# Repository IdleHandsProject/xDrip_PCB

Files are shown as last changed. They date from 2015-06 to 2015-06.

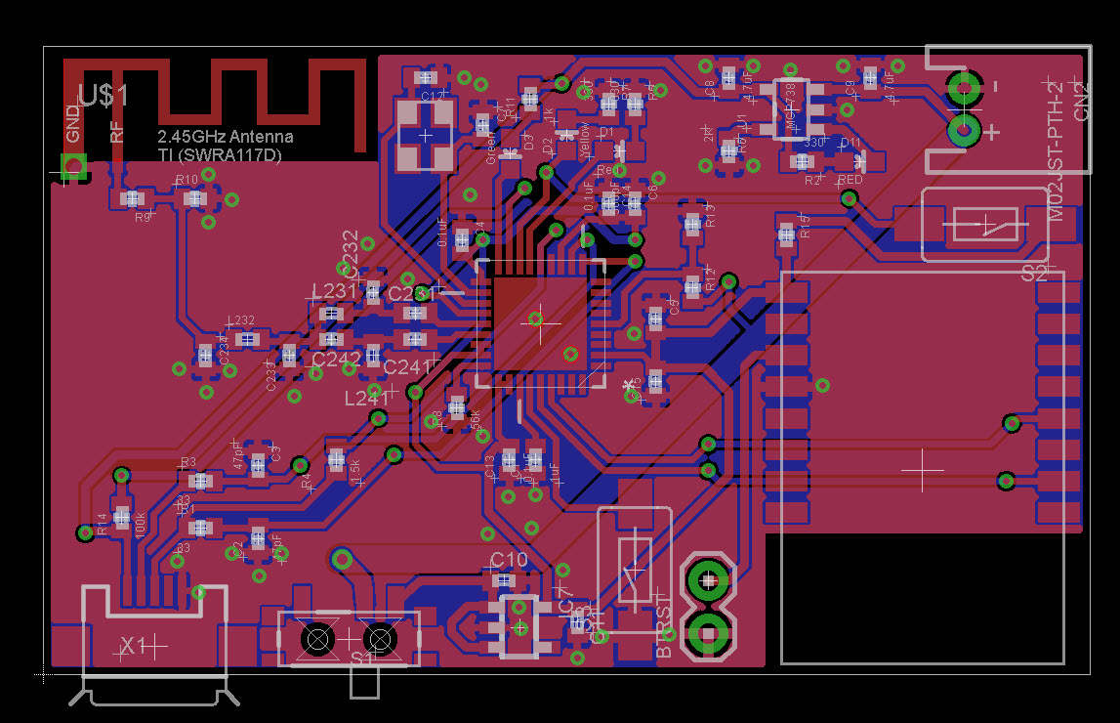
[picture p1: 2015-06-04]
DexDripLayout.jpg

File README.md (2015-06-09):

# xDrip_PCB

A custom PCB for the xDrip Project
<p>The xDrip project can be found here: http://stephenblackwasalreadytaken.github.io/xDrip/
Note: This board has not been tested. It is a WIP.
<p>Please don't go blindly ordering a board and expecting it to work. Go over the schematics yourself and confirm everything is correct. I will post an update when I have a working version.
<p>I am also working on a 3D printed case that will be available on shapeways, and I will be looking into mass producing the boards to reduce the costs. They will be fully completed boards. 
<p>I post updates on Twitter:  <a href="http://www.twitter.com/idlehandsdev">@idlehandsdev</a>

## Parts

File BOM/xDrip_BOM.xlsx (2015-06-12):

Qty | Value | Package | Parts | DIGIKEY PROD_ID
1 |  | SWITCH-SPST-SMD-A | S1 | 563-1102-1-ND
6 | 0.1uF | C0402 | C4, C5, C13, C14, C10, C11 | 587-1227-1-ND
3 | 1.2nH | C0402 | L231, L232, L241 | 587-1499-1-ND
1 | 1.5k | 0402-RES | R4 | P1.50KLCT-ND
1 | 1.5pF | 0402-CAP | C234 | 490-6213-1-ND
1 | 1.8pF | 0402-CAP | C233 | 712-1271-1-ND
1 | 100k | 0402-RES | R14 | P100KJCT-ND
2 | 100pF | 0402-CAP | C231, C241 | 490-5922-1-ND
1 | 1M | 0402-RES | R13 | P1.00MLCT-ND
1 | 1k | 0402-RES | R11 | P1.0KJCT-ND
2 | 1pF | 0402-CAP | C232, C242 | 587-1007-1-ND
1 | 1uF | 0402-CAP | C1 | 490-1320-1-ND
1 | 2K | 0402-RES | R6 | P2.00KLCT-ND
2 | 33 | 0402-RES | R1, R3 | P33.0LCT-ND
6 | 330 | 0402-RES | R2, R5, R7, R9, R10, R15 | RMCF0402JT330RCT-ND
2 | 33pF | 0402-CAP | C7, C12 | 490-5936-1-ND
2 | 4.7uF | 0402-CAP | C8, C9 | 490-5915-1-ND
1 | 470K | 0402-RES | R12 | RHM470KCDCT-ND
2 | 47pF | 0402-CAP | C2, C3 | 399-7796-1-ND
1 | 48mHz Abracon | 3.2X2.5MM | Y1 | 535-10282-1-ND
2 | 560pF | 0402-CAP | C6, C15 | 1276-1577-1-ND
1 | 56k | 0402-RES | R8 | RHM56.0KCDCT-ND
1 | CC2511F32RSP | QFN50P600X600X90-37N | U$11 | 296-22557-1-ND
1 | Green | LED-0603 | D3 | 160-1446-1-ND
1 | M02JST-PTH-2 | JST-2-PTH | CN2 | 455-1719-ND
1 | MCP73831 | SOT23-5 | U1 | MCP73831T-2ACI/OTCT-ND
1 | Micro USB | USB-MICROB | X1 | 609-4053-1-ND
2 | RED | LED-0603 | D1, D11 | 160-1445-1-ND
2 | SWITCH-MOMENTARY-2-SMD-1101NE | TACTILE-SWITCH-1101NE | S2, S3 | CKN10388CT-ND
1 | TLV71333DBV | SOT-23-5 | IC7 | 296-35591-1-ND
1 | Yellow | LED-0603 | D2 | 160-1434-1-ND

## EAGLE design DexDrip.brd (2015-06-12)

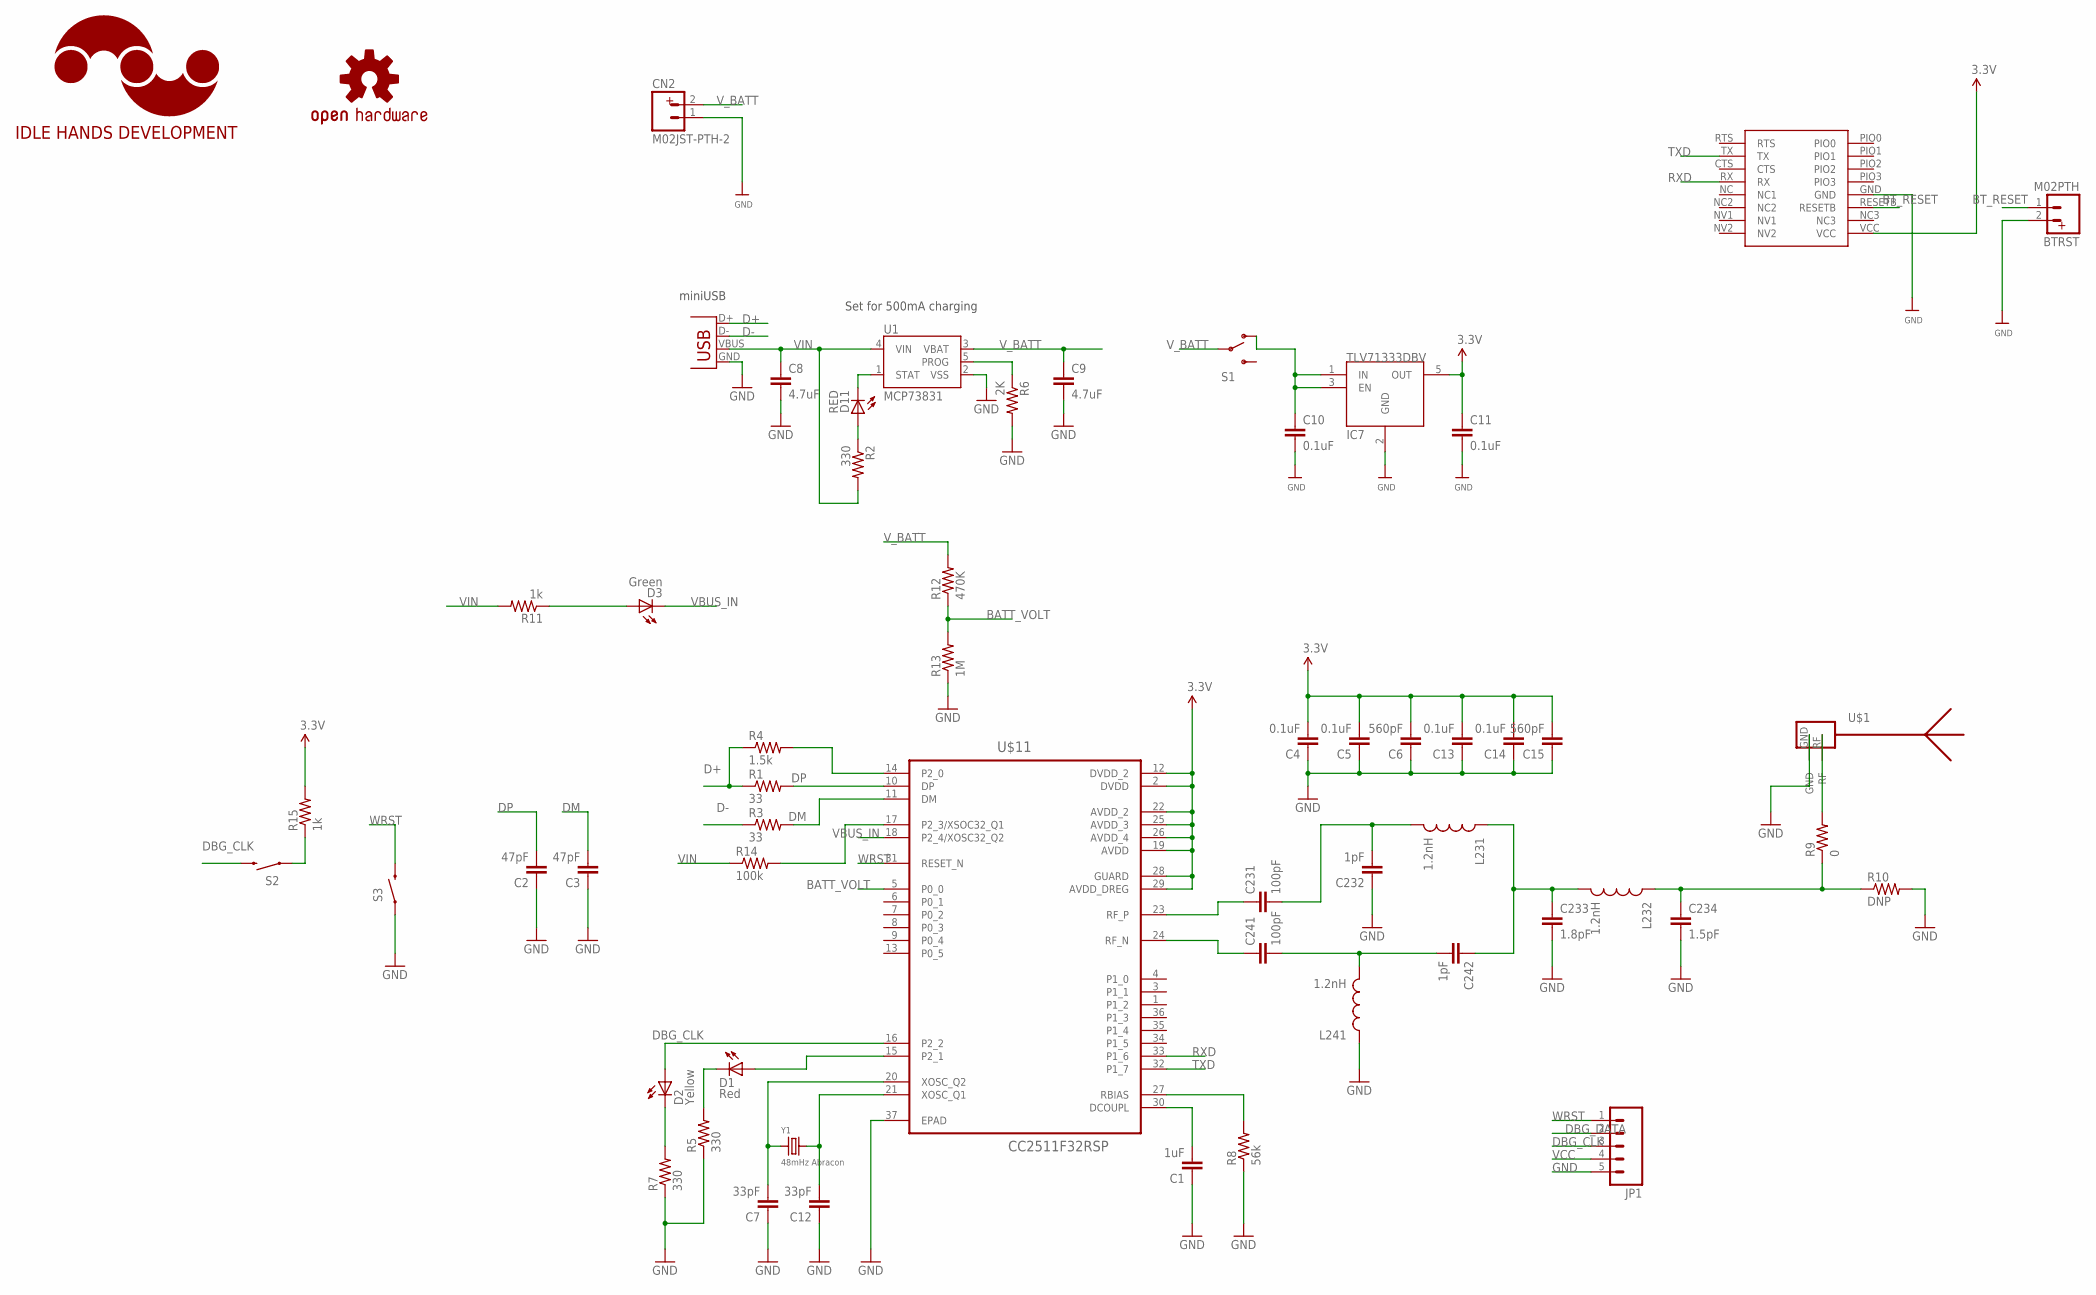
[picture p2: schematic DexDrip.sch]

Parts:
BTRST: M02PTH; 1X02
C1: 1uF; 0402-CAP
C2, C3: 47pF; 0402-CAP
C4, C5, C13, C14: 0.1uF; 0402-CAP
C6, C15: 560pF; 0402-CAP
C7, C12: 33pF; 0402-CAP
C8, C9: 4.7uF; 0402-CAP
C10, C11: 0.1uF; C0402
C231, C241: 100pF; 0402-CAP
C232, C242: 1pF; 0402-CAP
C233: 1.8pF; 0402-CAP
C234: 1.5pF; 0402-CAP
CN2: M02JST-PTH-2; JST-2-PTH
D1: Red; LED-0603
D2: Yellow; LED-0603
D3: Green; LED-0603
D11: RED; LED-0603
IC7: TLV71333DBV; SOT-23-5
JP1: M05LOCK; 1X05_LOCK
L231, L232, L241: 1.2nH; C0402
LOGO1: IDLEHANDS_LOGOS; IHD-LOGO-S
LOGO2: OSHW-LOGOS; OSHW-LOGO-S
R1, R3: 33; 0402-RES
R2, R5, R7: 330; 0402-RES
R4: 1.5k; 0402-RES
R6: 2K; 0402-RES
R8: 56k; 0402-RES
R9: 0; 0402-RES
R10: DNP; 0402-RES
R11, R15: 1k; 0402-RES
R12: 470K; 0402-RES
R13: 1M; 0402-RES
R14: 100k; 0402-RES
S1: SWITCH-SPDT-SMD-A; SWITCH-SPST-SMD-A
S2, S3: SWITCH-MOMENTARY-2-SMD-1101NE; TACTILE-SWITCH-1101NE
U1: MCP73831; SOT23-5
U$1: ANTENNA_1LEFT; SWRA117D_LEFT
U$2: BT_HM11; HM11
U$11: CC2511F32RSP; QFN50P600X600X90-37N
X1: Micro USB; USB-MICROB
Y1: 48mHz Abracon; 3.2X2.5MM

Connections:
BATT_VOLT: R12.1, R13.2, U$11.5 (P0_0)
BT_RESET: BTRST.1, U$2.RESETB
D+: R1.1, R4.1, X1.D+
D-: R3.1, X1.D-
DBG_CLK: D2.A, JP1.3, S2.P$2 (2), U$11.16 (P2_2)
DBG_DATA: D1.A, JP1.2, U$11.15 (P2_1)
DM: C3.2, R3.2, U$11.11 (DM)
DP: C2.2, R1.2, U$11.10 (DP)
GND: BTRST.2, C1.1, C2.1, C3.1, C4.1, C5.1, C6.1, C7.1, C8.2, C9.2, C10.2, C11.2, C12.1, C13.1, C14.1, C15.1, C232.1, C233.2, C234.2, CN2.1, IC7.2 (GND), JP1.5, L241.1, R5.1, R6.2, R7.1, R8.1, R10.2, R13.1, S3.P$1 (1), U1.2 (VSS), U$1.GND, U$2.GND, U$11.37 (EPAD), X1.GND
unnamed: R4.2, U$11.14 (P2_0)
unnamed: D3.A, R11.1
unnamed: R9.2, U$1.RF
unnamed: R8.2, U$11.27 (RBIAS)
unnamed: C1.2, U$11.30 (DCOUPL)
unnamed: C10.1, IC7.1 (IN), IC7.3 (EN), S1.1 (O)
unnamed: R14.2, U$11.17 (P2_3/XSOC32_Q1)
unnamed: R15.1, S2.P$1 (1)
unnamed: D1.C, R5.2
unnamed: D11.A, R2.1
unnamed: D2.C, R7.2
unnamed: C7.2, U$11.20 (XOSC_Q2), Y1.1
unnamed: C12.2, U$11.21 (XOSC_Q1), Y1.3 (2)
unnamed: C231.1, U$11.23 (RF_P)
unnamed: C231.2, C232.2, L231.2
unnamed: C241.1, U$11.24 (RF_N)
unnamed: C241.2, C242.2, L241.2
unnamed: C233.1, C242.1, L231.1, L232.2
unnamed: C234.1, L232.1, R9.1, R10.1
PROG: R6.1, U1.5 (PROG)
RXD: U$2.RX, U$11.33 (P1_6)
STAT: D11.C, U1.1 (STAT)
TXD: U$2.TX, U$11.32 (P1_7)
VBUS_IN: D3.C, U$11.18 (P2_4/XOSC32_Q2)
VCC: C4.2, C5.2, C6.2, C11.1, C13.2, C14.2, C15.2, IC7.5 (OUT), JP1.4, R15.2, U$2.VCC, U$11.2 (DVDD), U$11.12 (DVDD_2), U$11.19 (AVDD), U$11.22 (AVDD_2), U$11.25 (AVDD_3), U$11.26 (AVDD_4), U$11.28 (GUARD), U$11.29 (AVDD_DREG)
VIN: C8.1, R2.2, R11.2, R14.1, U1.4 (VIN), X1.VBUS
V_BATT: C9.1, CN2.2, R12.2, S1.2, U1.3 (VBAT)
WRST: JP1.1, S3.P$2 (2), U$11.31 (RESET_N)

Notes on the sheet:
Set for 500mA charging
miniUSB

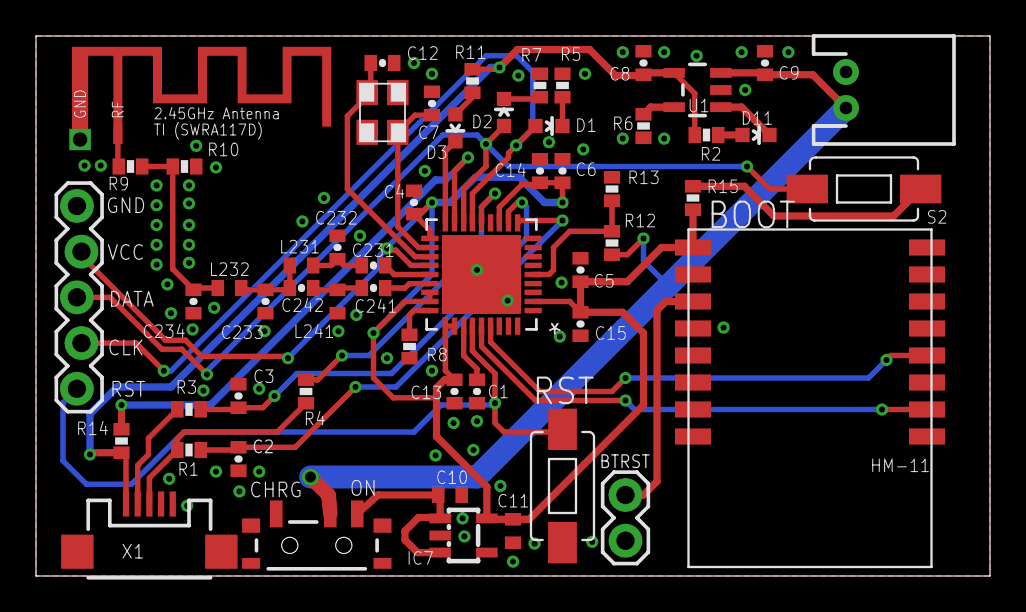
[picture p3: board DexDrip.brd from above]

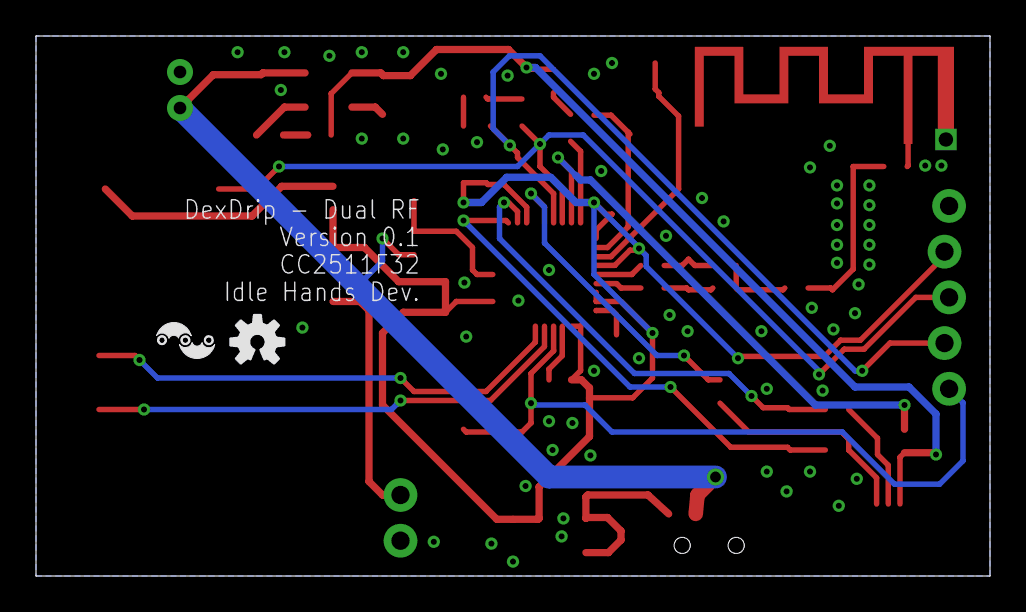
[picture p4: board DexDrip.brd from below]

Board: 2 copper layers, 53.0 x 30.0 mm, 58 parts (2 on the bottom side), 37 nets.

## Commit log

2015-06-04 First Upload
    [DexDrip.brd, DexDrip.sch]
2015-06-09 Added programming pins
    [DexDrip.brd, DexDrip.sch]
2015-06-09 Added BOM
    [DexDrip.brd, xDrip_BOM.xlsx]
2015-06-12 Fixed button part number
    [xDrip_BOM.xlsx]
2015-06-12 Fixes some R Values RF WORKING
    [DexDrip.brd, DexDrip.sch]
2015-06-12 words moved
    [DexDrip.brd]

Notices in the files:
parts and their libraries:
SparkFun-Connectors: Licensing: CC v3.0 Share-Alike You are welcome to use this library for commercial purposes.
